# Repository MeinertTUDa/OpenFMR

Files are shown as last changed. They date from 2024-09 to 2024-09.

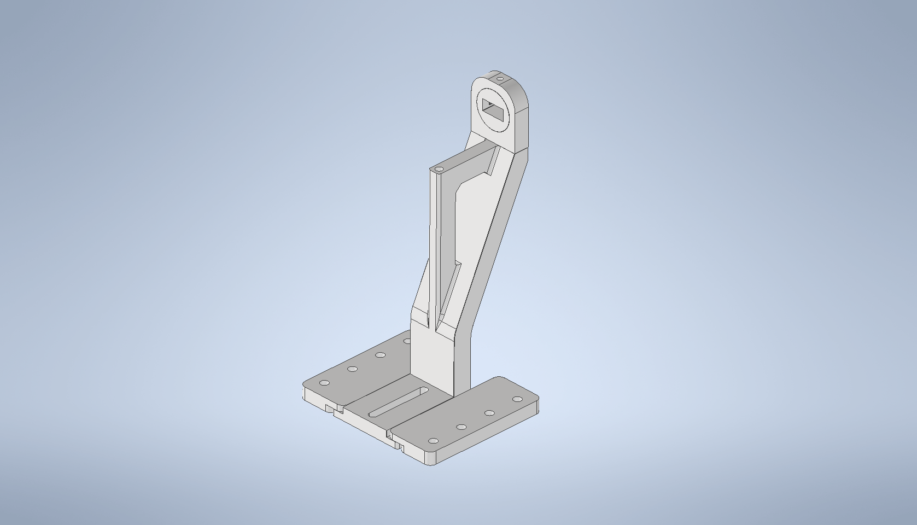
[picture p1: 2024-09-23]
3dprints/cpw_stand/assembly.png

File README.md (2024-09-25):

# OpenFMR
Open Ferromagnetic Resonance Broadband Spectrometer

The OpenFMR system enables broadband ferromagnetic resonance measurements with relatively cheap off-the-shelf components. It is capable of measuring the FMR of thin films as thin as 1nm of CoFeB and maybe even less.

setup

To assemble the system, you will have to get suitable hardware components, make some 3D prints, send the PCB layout files for production to obtain the grounded coplanar waveguide, and install the Python software on your computer. The software in this repository is optimized for usage with the following components:

- DS Instruments SG30000PRO RF signal generator
- Krytar 203BK Schottky detector
- Thorlabs KMM24 cables
- WithWave 2.92mm End Launch Connectors (Narrow Block)
- Zurich Instruments MFLI Lock-in Amplifier
- CAENels FAST-PS 1k5 50V 30A bipolar power supply
- Xiamen Dexing Magnet Tech DXWD-80 C-frame magnet
- Magnet-Physik FH55 gaussmeter
- 0.2mm wire (10m) for the modulation coils
- Kemo M032S audio amplifier for the modulation coils

The document Supplemental Material.pdf in the preprint folder contains a list of viable alternatives for the various components. In our design, the lock-in amplifier and the bipolar power supply for the electromagnet are two somewhat costly devices. These can be replaced with cheaper alternatives, such as a unipolar power supply for the magnet. The software will require modifications accordingly, which should be straightforward, though.

## Grounded Coplanar Waveguide
GCPW
The grounded coplanar waveguide is manufactured on a 200µm Rogers 4003C prepreg substrate. The manufacturing process should be performed as follows:
- attach to 1mm FR4 support
- mill the contour
- drill the blind via holes
- deposit copper
- etch the waveguide
- immersion tin surface finish (no Ni/Au plating!)

## Modulation Coils
modulation_coils
The modulation coils need a support structure, which we create by 3D printing. There are two different designs available, for in-plane and out-of-plane measurements, respectively. The 0.2mm copper magnet wire (10m long) is wound by hand onto the support structure and connected to stronger cables via screw terminals, which are mounted with M2 threaded inserts into the support structure. These are clamped between the tapered poles, which are supposed to have a 30mm pole cap diameter. For other pole shapes, the designs may have to be adapted or made from scratch. All 3D designs are available as Autodesk Inventor files.

A stand for the GCPW is also available as a 3D print. This will require modification with a different magnet. 

## Python Software
OpenFMR_GUI
The python based software requires a number of modules to work. It is advisable to use a recent version of the Anaconda package. The following modules have to be installed:
- PyQt5
- pyqtgraph
- zipfile
- numpy
- scipy
- matplotlib / pylab
- fnmatch
- pyserial
- zhinst

Set the device ports in fmr.py, the MFLI and the FastPS have IP interfaces, the SG30000PRO has a serial interface. It is advisable to run the IP devices on a separate network with a router or a switch and use static IP addresses. Correspondingly, the PC should be equipped with two networking interfaces.

Once the hardware is set up, a calibration file has to be obtained for the magnet, which relates the magnet current to the measured magnetic field in the pole gap. Use the calibrate_magnet.py script in the tools folder. Once this is done for both the in-plane and the out-of-plane modulation coils, you should be able to perform your first measurements!

OpenFMR_Data_Analysis

The data analysis software runs independently and requires a smaller number of dependencies. This can be run by the users on their personal computers. Measured data is stored in zip files, which also contain the analysis results. The data within the zip file container are easily accessible text files.

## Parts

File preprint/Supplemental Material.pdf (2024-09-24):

## OpenFMR: A low-cost open-source broadband ferromagnetic resonance spectrometer

## Supplemental Material

Markus Meinert, Tiago de Oliveira Schneider, Shalini Sharma, and Amir Khan
New Materials Electronics Group, Department of Electrical Engineering and Information Technology, Technical University of Darmstadt, Merckstr. 25, 64283 Darmstadt, Germany

### List of alternatives

Signal generator:
- DS Instruments SG30000PRO (up to 30GHz)
- DS Instruments SG40000L (25 to 40 GHz)
- AnaPico APSYN140 + FILT + TOUCH (up to 43.5 GHz)
- MiniCircuits SSG-30G-RC
- Berkeley Nucleonics Model 865 + FILT (up to 40GHz)
- Keysight N5183B
- Anritsu MG3695C or MG36241A
- Siglent SSG5085A
- Siglent SNA5032A (VNA to 26.5GHz)

Detector:
Packaged:
- Krytar 203BK
- Anritsu Model 75KC50
- Keysight 8474E + 2.4mm adapter + SMC-to-BNC adapter
- MW Devices mwdevices.com, Schottky with 2.92mm on request Do-it-yourself:
- ADL6010 (+ evaluation board! ADL6010-EVALZ)
- Infineon BAT62

Cables:
- Thorlabs KMM24
- Huber+Suhner Sucoflex 102 / 11SK / 11SK / 1000mm

Edge Launch Connectors available from:
- Southwest Microwave, Inc.
- WithWave
- Signal Microwave

Modulation Coils:
- Adafruit 2.5W Mono Amplifier
- Kemo M032S 12W Amplifier
- 0.2mm wire, 2x 10m

Lock-In Amplifier:
- Zurich Instruments MFLI
- Stanford Research System SR810, SR830, SR860
- Anfatec USB LockIn 250
- Dexing Magnet DXA-001C
- Signal Recovery 7230, 7265
- Femto LIA-MV-150
- Moku:Lab, Moku:Pro
- Redpitaya STEMlab or SDRlab
- OLIA (The Open Lock-In Amplifier), https://github.com/OpenLockIn/OLIA

Electromagnet:
- Xiamen Dexing DXWD-80 or DXWD-60
- GMW 5405 or 3480
- do-it-yourself

Electromagnet Power Supply:
- Caenels 30A 50V 1.5kW
- Dexing Magnet DX-F2030 1kW

Additional Electronics:
- Magnet-Physik Teslameter
- Keithley DMM6500
- Sonnecy CYTP Hall Probe

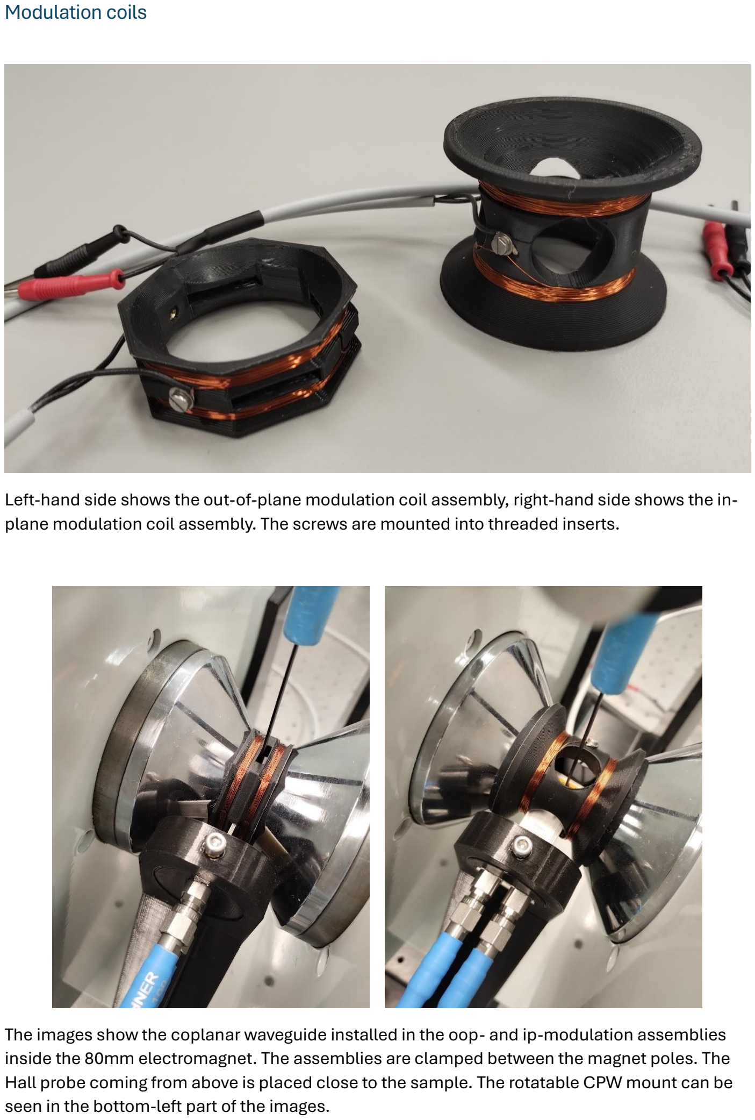
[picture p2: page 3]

### Modulation coils

Left-hand side shows the out-of-plane modulation coil assembly, right-hand side shows the in-plane modulation coil assembly. The screws are mounted into threaded inserts.

The images show the coplanar waveguide installed in the oop- and ip-modulation assemblies inside the 80mm electromagnet. The assemblies are clamped between the magnet poles. The Hall probe coming from above is placed close to the sample. The rotatable CPW mount can be seen in the bottom-left part of the images.

### Coplanar waveguide

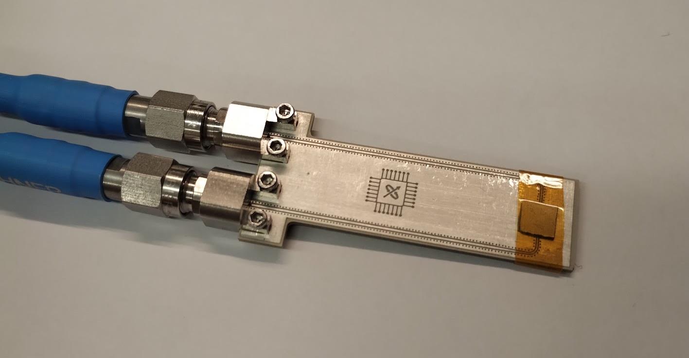
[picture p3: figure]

The image shows the sample mounted upside-down on the waveguide. Adhesive Kapton tape is used for fixing the substrate to the waveguide to hold it in position for the out-of-plane measurement.

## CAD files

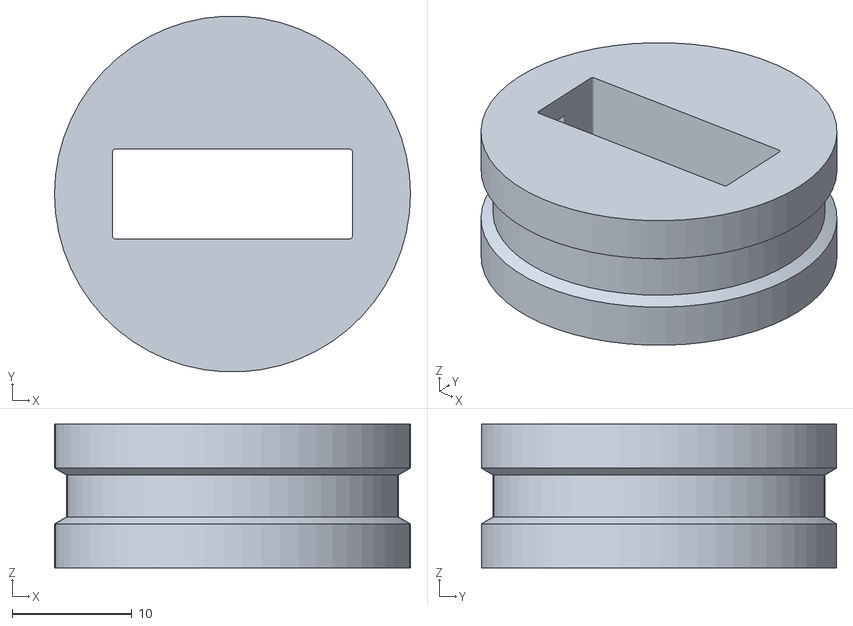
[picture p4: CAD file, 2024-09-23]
3dprints/cpw_stand/DXWD80_cpw_stand_C.stl
29.7 x 29.7 x 12.0

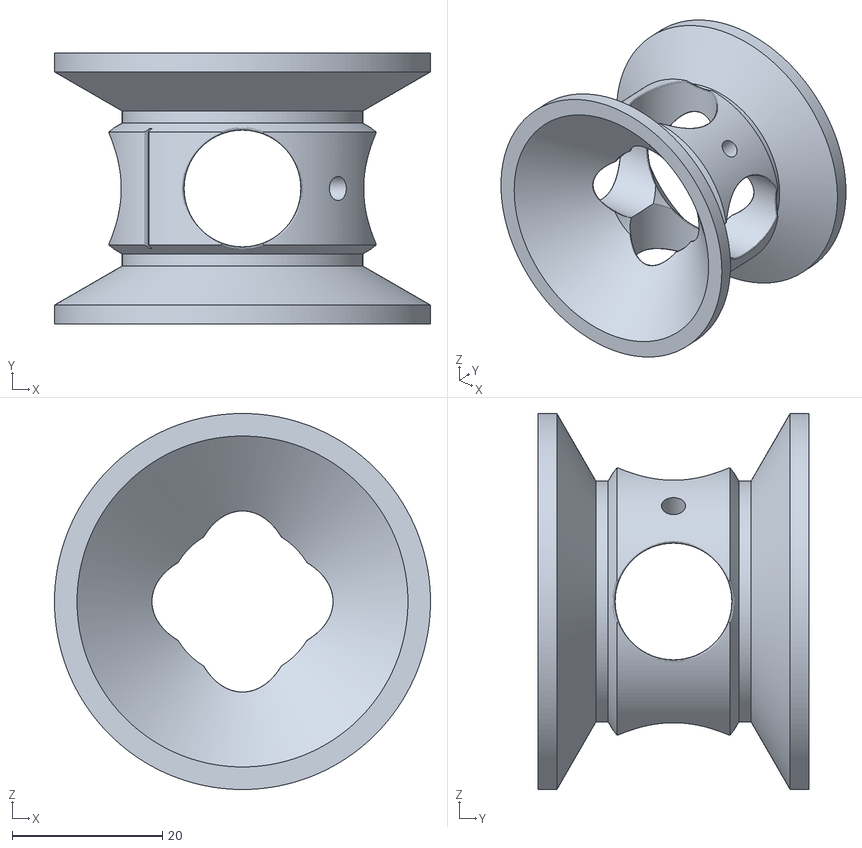
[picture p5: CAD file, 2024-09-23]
3dprints/modulation_coils/DXWD80_modulation_coil_support_20mm_InPlane.stl
50.0 x 36.0 x 50.0

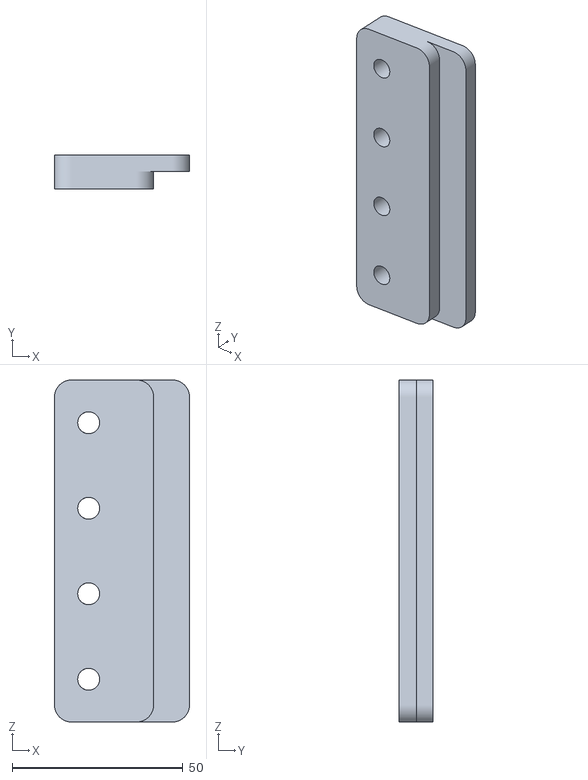
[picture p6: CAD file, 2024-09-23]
3dprints/cpw_stand/DXWD80_cpw_stand_D_2x.stl
39.5 x 10.0 x 100.0

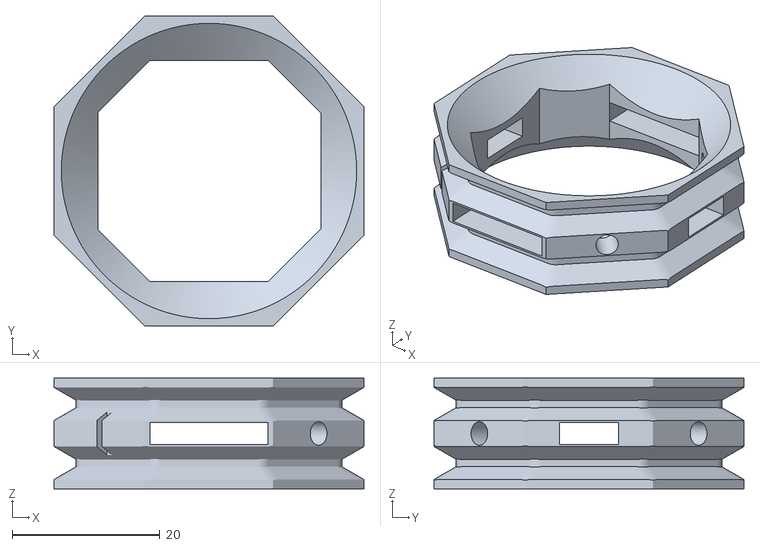
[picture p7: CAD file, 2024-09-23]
3dprints/modulation_coils/DXWD80_modulation_coil_support_5mm_OutOfPlane_OCTAGON.stl
42.0 x 42.0 x 15.0

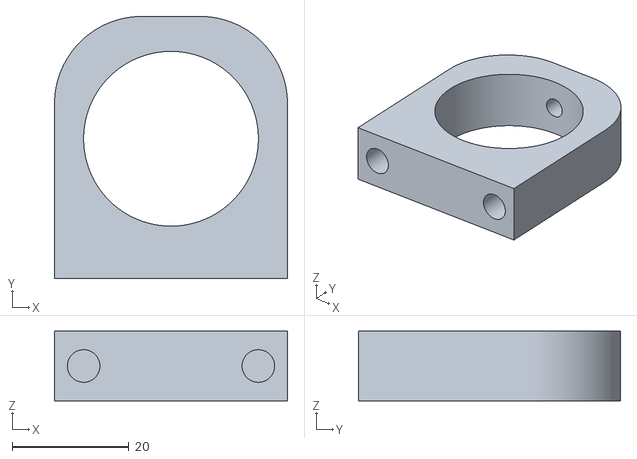
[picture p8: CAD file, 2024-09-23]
3dprints/cpw_stand/DXWD80_cpw_stand_B.stl
40.0 x 45.0 x 12.0

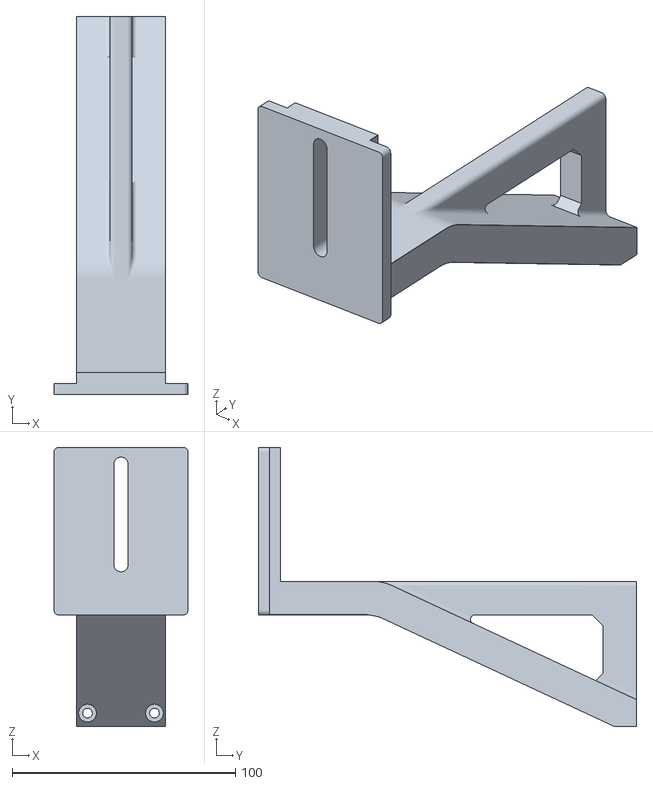
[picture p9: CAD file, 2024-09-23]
3dprints/cpw_stand/DXWD80_cpw_stand_A.stl
60.0 x 169.5 x 125.0

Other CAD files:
3dprints/cpw_stand/DXWD80_cpw_stand_A.ipt
3dprints/cpw_stand/DXWD80_cpw_stand_B.ipt
3dprints/cpw_stand/DXWD80_cpw_stand_C.ipt
3dprints/cpw_stand/DXWD80_cpw_stand_D_2x.ipt
3dprints/modulation_coils/DXWD80_modulation_coil_support_20mm_InPlane.ipt
3dprints/modulation_coils/DXWD80_modulation_coil_support_5mm_OutOfPlane_OCTAGON.ipt
